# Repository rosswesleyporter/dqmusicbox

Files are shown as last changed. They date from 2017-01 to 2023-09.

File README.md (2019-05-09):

# Dementia Friendly Music Player

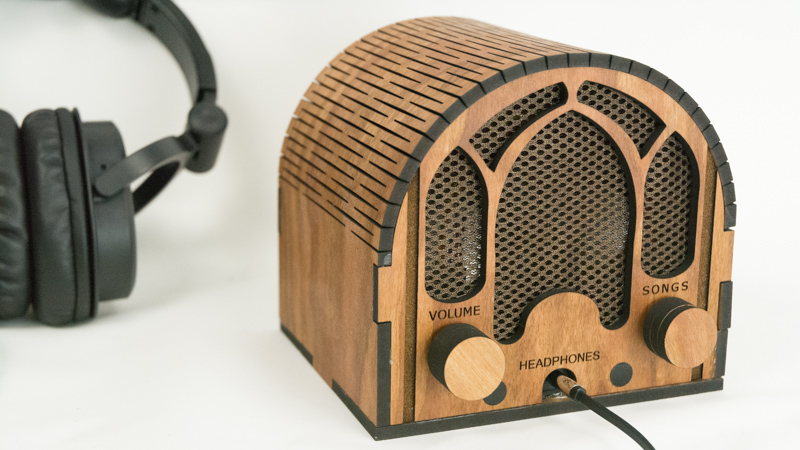
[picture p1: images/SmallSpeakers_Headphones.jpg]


I was inspired by the documentary Alive Inside, which shows the profound joy that music can bring to people with dementia. But my Dad could no longer operate CD players or iPods. But he could use this, because it operates like a familiar 1940s radio (but with a Pi & music files inside). 

Goals: 
1. Bring the joy of music to those dementia 
2. Bring the joy of meaningful giving to makers 

47 million people worldwide have dementia. People with dementia often travel back in time by literally forgetting the most recent decades (and modern tech). Thus the vintage user interface of this device. 

The build process is easy -- no soldering, no woodworking. You can make this. Kids can make this.

You can choose between a wood enclosure (photo above) or a 3D printed enclosure. Special thanks to Trey Bagley for designing the gorgeous retro-style 3D printed enclosure.

Everything you need is in this repository e.g. software, build instructions, laser cutting (wood) files, and 3D printing files, detailed step-by-step build instructions with photos. If you have a laser cutter or a 3D printer, you can do this at home. Alternatively, you can send the files to an online service of your choice to laser cut or 3D print the enclosure.

For more information, see http://DementiaMusicPlayer.org.

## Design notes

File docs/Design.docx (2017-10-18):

# DQMusicBox: Design

17 October 2017

# 1 About this document

This document specifies the design for a dementia-friendly music player called DQMusicBox. It is an open source project. This document exists so other people can modify or improve on DQMusicBox. If you want to make a DQMusicBox from the existing design, you don’t need this document – you can follow the existing build instructions (readme.pdf).

# 2 Discussion

Let’s start where we left off in the requirements document – with some of the challenging use-cases. I have added a few key sentences about the design.

Use case | Challenge

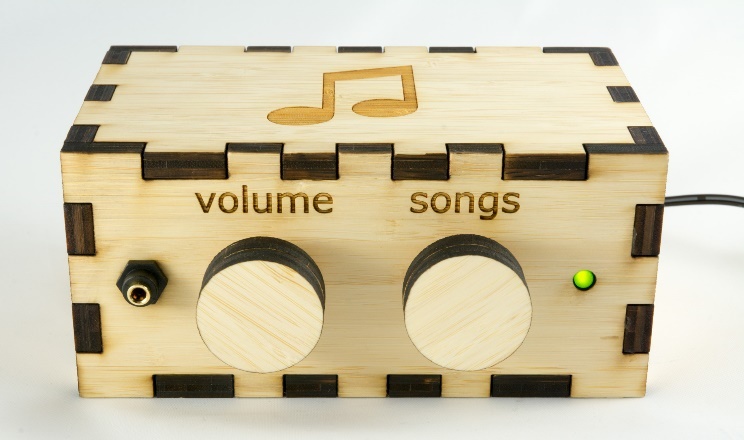
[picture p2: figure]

[End-user] Be familiar | The device should immediately seem familiar to the user. For instance, by resembling a vintage radio or a vintage phonograph (you may have better ideas than these). Design: Vintage radio.

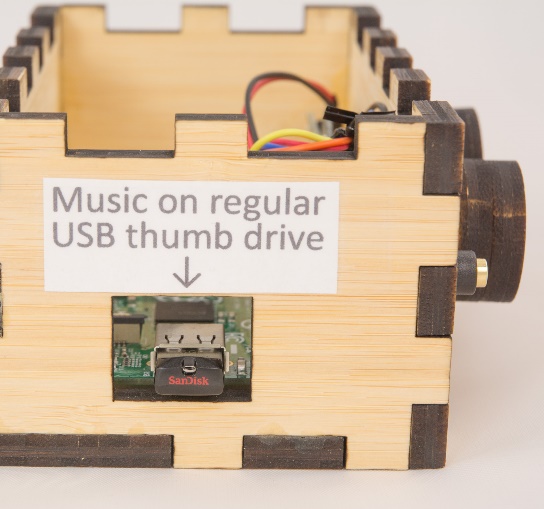
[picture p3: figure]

[Caregiver] Update the set of music | The caregiver may be a non-technical elderly spouse. Thus, mucking with micro-SD cards may not be the best choice. Design: An externally accessible normal USB thumb drive holds the music and only the music (the operating system and programs are stored elsewhere).
[System] Play key music formats | It’s helpful for the caregiver if the system supports a variety of music formats e.g. MP3, AAC/iTunes, FLAC. Design: VLC (https://www.videolan.org/vlc/index.html) (specifically VLC-NOX) handles the playback, so all of the above formats are supported.
[System] Create playlist | Create a playlist in some sensible order e.g. alphabetical by album/folder name. Design: My code scans the USB thumb drive, orders found music by album/folder name, and then hands this off as a single playlist to VLC-NOX.
[System] Have good audio quality | The sound quality should at least be good. It doesn’t have to be amazing, but it shouldn’t be aggravating. Design: The system uses a firmware update (https://www.raspberrypi.org/forums/viewtopic.php?f=29&t=136445) from the Raspberry Pi Foundation that dramatically improves audio quality, details below.
[System] support sudden shutdown | The device should behave like a consumer electronics device e.g. you can unplug it with no issues. Design: The system uses a read-only micro-SD card. More specifically, a TMP_WRITE_PROTECT (https://www.seanet.com/~karllunt/sdlocker.html) micro-SD card.

# 3 Key hardware components

## 3.1 List of hardware components

For a full list of hardware components, see the build instructions (readme.pdf). Below are a few of the key hardware components.

## 3.2 How did you choose key components?

When my wife asks me a question, sometimes I say, “It’s a long nerdy answer, do you really want to know?”. Then she usually leaves the room. Do you want to know the long answer? If so, read on. The choice was largely driven by satisfying the above challenging use-cases. And by cost. And I used the decision grid table below. The decision grid is 1.5 years out of date, but gives you a sense.

| Parts cost including case | Ease of loading music | Unpluggable? | Quick boot? | Software effort | Hardware design effort | Soldering | Support | audio quality | Total | Notes
Score range | 3 = $50 or less 2 = $65 or less 1 = $80 or less 0 = $95 or less | 2 = USB flash 1 = ext SD 0 = int SD | 2 = safe 1 = mostly safe 0 = crashola | 1 = instant 0 = <1 min | 2 = no coding 1 = some coding 0 = all coding | 2 = none 1 = some 0 = all | 2 = little 1 = some 0 = lots | 2 = great 1 = OK 0 = none
Score weight | 2 | 1 | 1 | 1 | 1 | 2 | 1 | 1
Pi 2 (https://www.raspberrypi.org/products/raspberry-pi-2-model-b/) | 1 | 2 | 1 | 0 | 2 | 2 | 2 | 2 | G | 15
Pi A+ (https://www.raspberrypi.org/products/model-a-plus/) | 2 | 1 | 1 | 0 | 2 | 2 | 2 | 2 | G | 16
Pi Zero (https://www.raspberrypi.org/products/pi-zero/) | 3 | 1 | 1 | 0 | 2 | 2 | 0 | 2 | G | 16
Banana Pi (http://www.s-config.com/goodbye-raspberry-pi-hello-banana-pi/) | 1 | 2 | 1 | 0 | 1 | 2 | 2 | 1 | G | 13
Arduino + Adafruit MP3 shield (https://www.adafruit.com/products/1790) | 1 | 1 | 2 | 1 | 0 | 2 | 0 | 2 | G | 12 | MP3 shield is $30.
Arduino + Sparkfun MP3 shield (https://www.sparkfun.com/products/12660) | 1 | 1 | 2 | 1 | 0 | 2 | 0 | 2 | G | 12 | MP3 shield is $35.
Arduino + Elechouse MP3 shield (http://www.gearbest.com/boards-shields/pp_241522.html?currency=USD) | 2 | 2 | 2 | 1 | 0 | 2 | 2 | 1 | G | 16 | MP3 shield is $20. Poor playlisting.
Sparkfun Lilypad (https://www.sparkfun.com/products/11013) | 0 | 0 | 2 | 1 | 0 | 2 | 1 | 2 | G | 10 | Lilypad is $50.
Custom standalone circuit (http://pcbshopper.com/) | 3 | 2 | 2 | 1 | 2 | 0 | 1 | 1 | G | 15
MP3 hardware player | | | | | | | | | | | Can't find good one
Pine64 (http://pine64.com/) | 3 | 2 | 1 | 0 | 1 | 2 | 2 | 1 | ? | 16 | Has headphone jack.
C.H.I.P. (http://getchip.com) | 3 | 2 | 1 | 0 | 1 | 2 | 2 | 1 | ? | 16 | $9. Has headphone jack.
Orange Pi PC (http://hackaday.com/2015/09/05/orange-is-the-new-15-pi/) | 2 | 2 | 1 | 0 | 1 | 2 | 2 | 0 | N | 14 | OK built-in audio
Odroid C1+ (http://www.hardkernel.com/main/products/prdt_info.php?g_code=G143703355573) | | | | | | | | | | | No headphone jack.

## 3.3 Raspberry Pi 1 Model A+

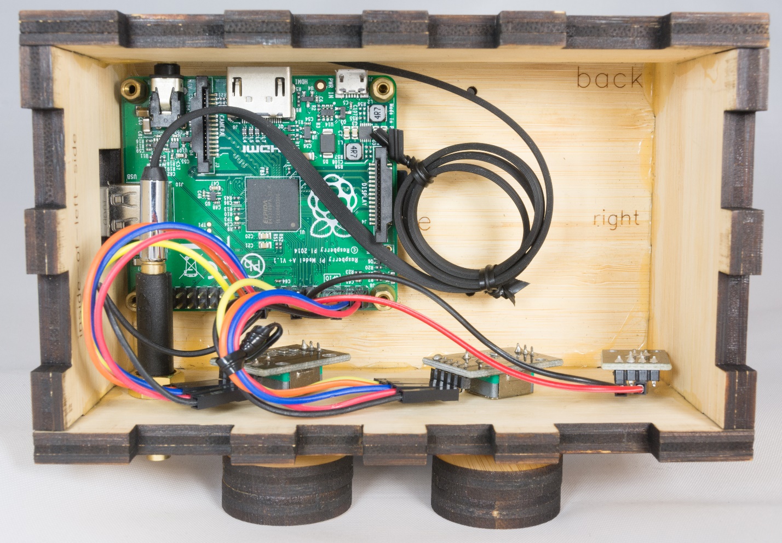
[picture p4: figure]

- Why Pi? A Pi satisfied the challenging use-cases above.
- Why Pi A+? Cheapest Pi model that has a headphone jack and populated USB headers.

## 3.4 KY-040 rotary encoder

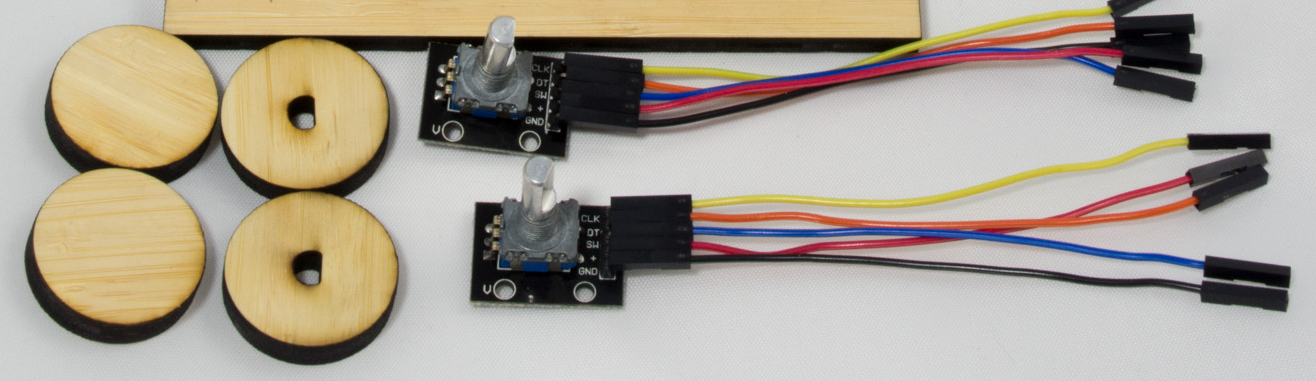
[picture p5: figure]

- Why?
  - No soldering required! Just jumper wires.
  - Performs well.

## 3.5 Making the micro-SD card reliable -- TMP_WRITE_PROTECT

The micro-SD card is the weak link in Raspberry Pi based solutions. For instance, micro-CD cards can get corrupted when power is lost during a write. But what if we didn’t need to write? That is the case here – the DQMusicBox doesn’t need to change. DQMusicBox is a fixed function device – it doesn’t have to evolve. So the micro-SD card can be read-only. Raspbian doesn’t really want to be read-only. But I don’t care if Raspbian is unhappy. I only care if it works.

The answer is the TMP_WRITE_PROTECT feature that is part of the SD card spec. It is fiendish. It accepts write requests (like Raspbian wants), but it puts all such writes in a special place. And those writes are thrown away when power is lost or when the device is rebooted. So no worries, if power is lost during a write. And if you want to factory reset a DQMusicBox? Just unplug it. References:

  - SD Card Write Protection (http://www.bertold.org/sdtool/)
  - Build the SD Locker and Make Your SD Cards More Secure

I know of two methods to enable TMP_WRITE_PROTECTION:

1. Building the SD locker project on Hackaday (https://d.docs.live.net/607157b747fa4bbf/Documents/projects/dqmusicbox_working/docsource/Build%20the%20SD%20Locker%20and%20Make%20Your%20SD%20Cards%20More%20S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).
2. Follow Appendix 1 in this project’s build instructions. The essence of it is to use a Pi 3, booted from USB, using the SD Card Write Protection (http://www.bertold.org/sdtool/) too. This is the method that I used.

# 4 Software stack (component diagram)

I like to think of myself as intelligently lazy. And I think that I achieved that here. The project makes good use of existing code. In particular, VLC does a lot of the work. I wrote a shell script and ~300 lines of Python. Thanks to Bob Rathbone (http://bobrathbone.com/) for his excellent tutorial on rotary encoders and for his GPL’ed code (http://www.bobrathbone.com/raspberrypi/Raspberry%20Rotary%20Encoders.pdf).

# 5 Use-case implementation

I’ve already covered the challenging use-cases. Here are the others.

## 5.1 End-user

Name | Description
Start song | Turn a knob, any knob
Change song | Turn the songs knob – clockwise for next, anti-clockwise for previous
Change volume | Turn the volume knob

## 5.2 Caregiver

Name | Description
Pause music | Tap either knob.
Update the set of music | Use a PC or Mac to add or remove albums/folders from the USB thumb drive.

## 5.3 Builder

Name | Description
Support builders that are not woodworkers | We don’t need no stinking jigsaws, we have lasers! The case is laser cut, pieces just need to be glued together. You can send the design to a company that does the laser cutting for you for $28.
Support builders that are not good at soldering | No soldering required. The key was finding rotary encoders that don’t require soldering.

## 5.4 System

Name | Description
Be secure | This is not an Internet of Things device. This is a thing. It never has to be online, it never has to be exposed to nasty things like hackers and reality television.

# 6 Wiring diagram

# 7 Case design

The requirements and key elements of the design for the case:

- Keep with the theme of vintage radio
- Use a laser-cutter approach, so no woodworking skills are required
- Make it possible to send off the design to a company (e.g. Ponoko) for laser cutting (not everyone has access to a laser cutter)
- No staining, painting, or other finishing required
- Include engraving (“volume”, “songs”, and the musical note)
- Include knobs
- Wood thicker than the screw threads of the standoffs (the screws that hold the Pi in place)
- Not too expensive

The result is a design intended to be laser-cut from two pieces of 181x181mm 6.7mm thick amber bamboo (https://www.ponoko.com/make-and-sell/show-material/567-bamboo-blonde-3-ply):

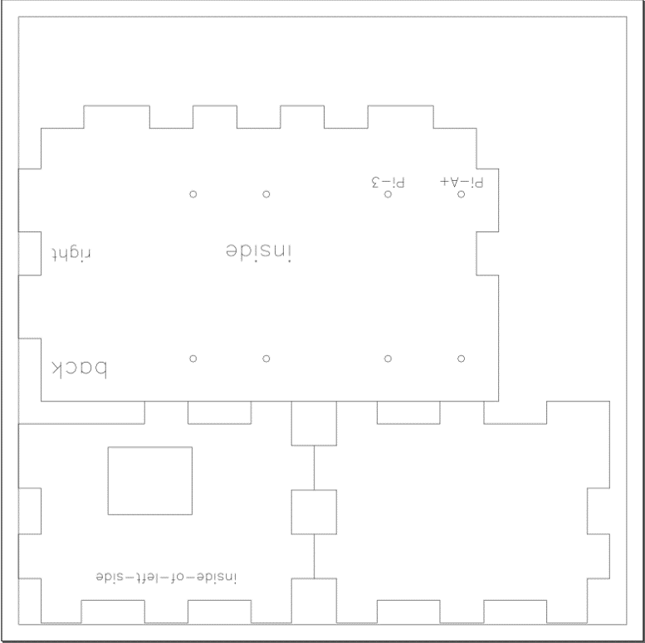
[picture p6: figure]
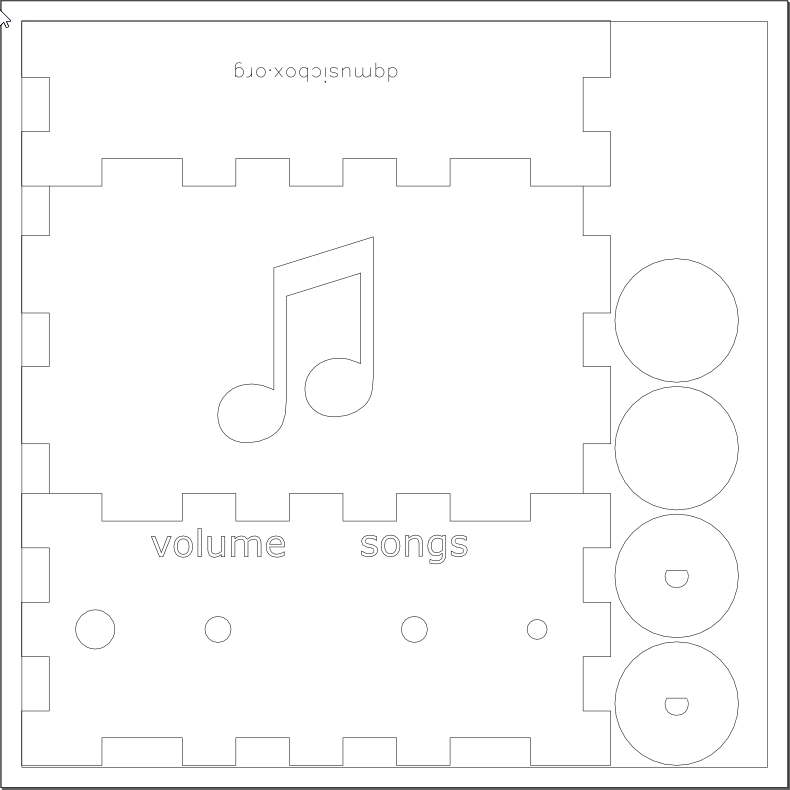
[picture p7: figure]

The actual case design can be found in github (https://github.com/rosswesleyporter/dqmusicbox/tree/master/case).

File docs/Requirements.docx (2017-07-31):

# DQMusicBox: Requirements

30 July 2017

# 1 About this document

This document specifies the requirements for a dementia-friendly music player called DQMusicBox. It is an open source project. This document exists so other people can modify or improve on DQMusicBox. If you want to make a DQMusicBox from the existing design, you don’t need this document – you can follow the existing build instructions (readme.pdf).

# 2 Why I created this project

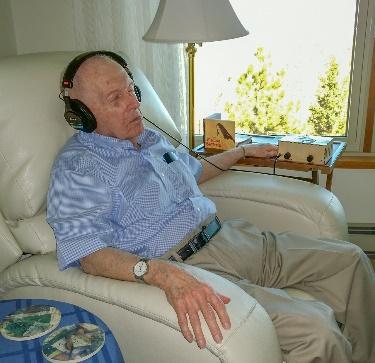
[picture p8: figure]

That’s DQ in the photo – my Dad. I was inspired by the documentary Alive Inside (http://www.aliveinside.us/) -- it suggests that people with dementia come alive when listening to their favorite music. Following that suggestion, I put DQ’s favorite music on an iPad. There was sustained joy on his face – joy from the familiar music and joy from the fact that nothing else in the frustrating world mattered for a few minutes. Unfortunately, he could no longer operate a traditional stereo or an iPad. Happily, he could use the music box that I later made for him.

# 3 The end-user’s special requirements

## 3.1 The device must feel familiar – no new learning

A key hypothesis is that the end-user interface must be simple and familiar. In other words, it needs to be easy *and* not require new learning. Every person with dementia is different, but it is common for the old memories to be stronger than the new memories. Thus, the device would ideally be familiar in the sense of being like a device from the end-user’s youth e.g. a vintage radio or a vintage phonograph. You may not agree with this hypothesis, and that’s OK -- you may also have different ideas or requirements. But this hypothesis is part of my requirements, so I’m making it clear.

## 3.2 The end-user needs a playlist of favorites, not a vast library

The end-user doesn’t need to have a lot of music on the device at any given time. Perhaps 50 old favorite songs. In modern terms, the end-user needs a playlist. Happily, this means that music selection is easier to implement – fewer songs to scroll through or otherwise navigate through. That said, the caregiver will want to change the set of music from time to time. By contrast, you probably use a cloud music service and have access to essentially an unlimited number of songs. That is a much harder navigation problem.

# 4 Use-cases

## 4.1 End-user

To keep things easy for the end-user with dementia, there are only three end user use-cases.

Name | Description
Be familiar | The device should immediately seem familiar to the user. For instance, by resembling a vintage radio or a vintage phonograph (you may have better ideas than these).
Start song | Start music playing
Change song | For instance, go to next song or prior song
Change volume | Make louder or softer

## 4.2 Caregiver

The caregiver is whoever setups up the device or helps the end-user with the device.

Name | Description
Pause music | Ideally should be possible both explicitly (e.g. a button press) and automatically (e.g. an automatic time-out).
Update the set of music | Add/remove music, including when preparing the device for first use. The caregiver will want to change the set of music from time to time, but not necessarily often.

## 4.3 Builder

This is a DIY project, so there is a builder. You may disagree, but I want as many people as possible to be able to build this. Thus:

Name | Description
Support builders that are not woodworkers | The DIY build plans should not require woodworking skills or woodworking tools.
Support builders that are not good at soldering | The DIY build plans should not require soldering skills or soldering tools.

## 4.4 System

Name | Description
Have good audio quality | Sound quality should be at least good.
Create playlist | The songs should play in some sensible order e.g. alphabetical by album name. In other words, the system needs to scan for music files and put them in some sensible order.
Play key music formats | e.g. MP3, AAC/iTunes, FLAC
Support sudden shut down | The device should tolerate being unceremoniously unplugged. That is, it should behave like any other consumer audio device.
Be secure | The device should have a known security plan. That plan could be that the device is not connected to a network. If the device runs a full operating system (Linux, Windows, …) and is connected to a network then it should get regular security patching, ideally without caregiver intervention.

# 5 Discussion

The need is simple, so the requirements are short. But there are challenges implied by these requirements.

Use case | Challenge
[Caregiver] Update the set of music | The caregiver may be a non-technical elderly spouse. Thus, mucking with micro-SD cards may not be the best choice. A USB thumb drive could be OK.
[System] Play key music formats | It’s helpful for the caregiver if the system supports a variety of music formats e.g. MP3, AAC/iTunes, FLAC. Not a problem if the device uses a full operating system e.g. Raspbian. But it is challenging for MP3 player boards and Arduino.
[System] Create playlist | Create a playlist in some sensible order e.g. alphabetical by album/folder name. Sounds easy, ya? And it is in the context of a full operating system e.g. Raspbian. It is surprisingly not straightforward for MP3 player boards and Arduino.
[System] Have good audio quality | The sound quality should at least be good. It doesn’t have to be amazing, but it shouldn’t be aggravating. This is not a problem for most technology options, but it is a challenge for some.
[System] support sudden shutdown | The device should behave like a consumer electronics device e.g. you can unplug it with no issues. This is no problem for MP3 player boards and Arduino. If the device includes a battery, it’s also no problem for a full operating system e.g. Raspbian. If the device does not have a battery, then sudden shutdown is a challenge for a full operating system. Because this is a fixed-function device, one option is for the executable bits to be on a read-only device (to resist corruption), keeping the music on a separate writeable device.

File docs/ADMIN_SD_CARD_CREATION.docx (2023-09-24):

# Dementia Friendly Music Player: How to prepare the micro-SD card image

24 September 2023

# 1 Introduction

This document describes how to create a Dementia Friendly Music Player system image – a .img file. I (Ross) am probably the only person that needs this document. Mostly people making a Dementia Friendly Music Player will use the fruit (the .img file) of the process described here -- you don’t need to create your own custom .img file unless you really want to.

# 2 No warranty

USE THESE DEMENTIA FRIENDLY MUSIC PLAYER (DQMUSICBOX) PLANS AND SYSTEM AT YOUR OWN RISK. THE DEMENTIA FRIENDLY MUSIC PLAYER PLANS ARE PROVIDED AS IS WITHOUT WARRANTY OF ANY KIND EITHER EXPRESSED OR IMPLIED, INCLUDING, BUT NOT LIMITED TO, THE IMPLIED WARRANTIES OF MERCHANTABILITY AND FITNESS FOR A PARTICULAR PURPOSE. THE ENTIRE RISK AS TO THE QUALITY AND PERFORMANCE OF THE PLANS AND SYSTEM IS WITH YOU. SHOULD THE PLANS OR SYSTEM PROVE DEFECTIVE, YOU ASSUME THE COST OF ALL NECESSARY SERVICING, REPAIR OR CORRECTION. IN NO EVENT WILL ANY PARTY BE LIABLE TO YOU FOR DAMAGES, INCLUDING ANY GENERAL, SPECIAL, INCIDENTAL OR CONSEQUENTIAL DAMAGES ARISING OUT OF THE USE OR INABILITY TO USE THE PLANS OR SYSTEM.

# 3 To create built-in headphone jack version

The Dementia Friendly Music Players below use the Pi’s built-in headphone jack.

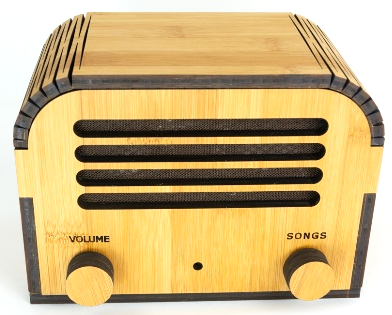
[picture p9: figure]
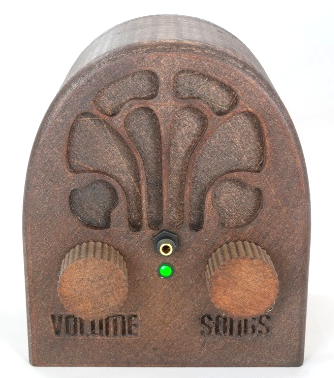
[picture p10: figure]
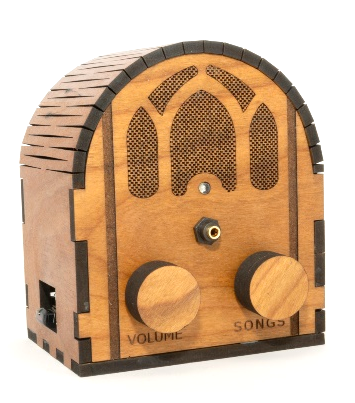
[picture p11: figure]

## 3.1 Flash DietPi onto the micro-SD card

Install DietPi i.e. follow these instructions: https://dietpi.com/docs/install/. I used DietPi 8.21.0 which was current as of this writing in September 2023. I used balenaEtcher (https://etcher.io/) (free) to write the disk image to the micro-SD card. This may take a while as the system updates itself.

## 3.2 Boot & configure DietPi

Put the Pi on Ethernet. Move the micro-SD card to the Pi, boot DietPi. After a build process (which will take a while), you will be prompted to make some choices.

DietPi-Config

Audio Options: Enable : Install ALSA to enable audio capabilities

Audio Options: Sound Card : Onboard 3.5mm output

DietPi-Software

Hardware Projects : Python 3 RPi.GPIO

System: ALSA : Advanced Linux Sound Architecture

Development : Git : clone and manage …

Development : Python 3: Runtime system, pip package installer, …

Install

## 3.3 Install pmount

sudo apt-get install pmount

## 3.4 Install VLC (music player)

sudo apt-get install vlc-bin

sudo apt-get install vlc-plugin-base

## 3.5 adduser pi

sudo adduser pi

## 3.6 Install/clone dqmusicbox, enable

cd /home/pi

git clone --depth 1 https://github.com/rosswesleyporter/dqmusicbox/

sudo chmod 755 dqmusicbox/bin/dqmusicbox.py

## 3.7 Install Python bindings for VLC

cd /home/pi

sudo git clone https://github.com/oaubert/python-vlc

cp python-vlc/generated/2.2/vlc.py dqmusicbox/bin

chmod 755 dqmusicbox/bin/vlc.py

## 3.8 Add shell script to automatically start dqmusicbox

cd /home/pi

sudo cp dqmusicbox/bin/dqmusicbox.sh /etc/init.d

sudo chmod 755 /etc/init.d/dqmusicbox.sh

sudo update-rc.d dqmusicbox.sh defaults

For more information, see Stephen Christopher Phillips’ terrific page (http://blog.scphillips.com/posts/2013/07/getting-a-python-script-to-run-in-the-background-as-a-service-on-boot/).

## 3.9 Configure such that USB drives mount automatically

The instructions below are from pauliucxz (https://raspberrypi.stackexchange.com/users/66022/pauliucxz) in StackExchange 66169 (https://raspberrypi.stackexchange.com/questions/66169/auto-mount-usb-stick-on-plug-in-without-uuid), preserved below for clarity. I am quite thankful for that answer. The first USB drive will automatically mount as /media/usb1.

Specify a udev rule by creating file /etc/udev/rules.d/usbstick.rules

ACTION=="add", KERNEL=="sd[a-z][0-9]", TAG+="systemd", ENV{SYSTEMD_WANTS}="usbstick-handler@%k"

Configure a system service by creating file /lib/systemd/system/usbstick-handler@.service

[Unit]

Description=Mount USB sticks

BindsTo=dev-%i.device

After=dev-%i.device

[Service]

Type=oneshot

RemainAfterExit=yes

ExecStart=/usr/local/bin/cpmount /dev/%I

ExecStop=/usr/bin/pumount /dev/%I

Create the mount script file /usr/local/bin/cpmount

#!/bin/bash

if mountpoint -q /media/usb1

then

if mountpoint -q /media/usb2

then

if mountpoint -q /media/usb3

then

if mountpoint -1 /media/usb4

then

echo "No mountpoints available!"

#You can add more if you need

else

/usr/bin/pmount --umask 000 --noatime -w --sync $1 usb4

fi

else

/usr/bin/pmount --umask 000 --noatime -w --sync $1 usb3

fi

else

/usr/bin/pmount --umask 000 --noatime -w --sync $1 usb2

fi

else

/usr/bin/pmount --umask 000 --noatime -w --sync $1 usb1

fi

Make the script executable

sudo chmod 755 /usr/local/bin/cpmount

## 3.10 Reboot

sudo reboot

## 3.11 Test

Make sure the music plays…

## 3.12 Shutdown

Provided that the reboot went well, shutdown:

sudo shutdown –h now

Then remove the micro-SD card.

## 3.13 Use Win32DiskImager to create the master image

Remove the micro-SD card from your Pi and place in the card reader of your computer. Use Win32DiskImager to create an image of Dementia Friendly Music Player that you just nicely configured.

# 4 To create USB DAC version

The Dementia Friendly Music Player that looks like this uses a USB DAC.

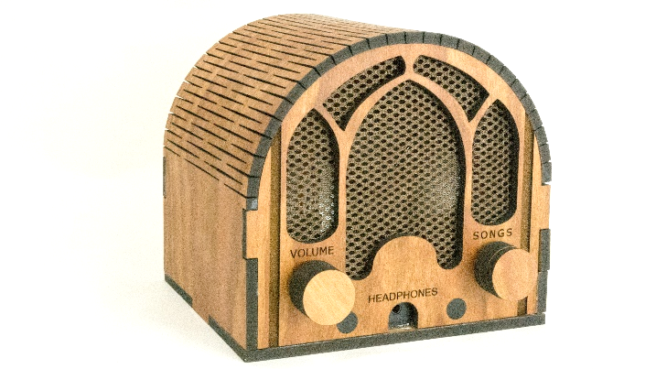
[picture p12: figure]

Use the image that you created above for the headphone version and make this change:

dietpi-config

Audio Options: Sound Card : USB Audio DAC (any)

Remove the micro-SD card from your Pi and place in the card reader of your computer. Use Win32DiskImager to create an image of Dementia Friendly Music Player that you just nicely configured.

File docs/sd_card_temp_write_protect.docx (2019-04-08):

# How to Write Protect an SD Card

7 April 2019, http://DementiaMusicPlayer.org, Ross Porter rosswesleyporter@gmail.com

## About SD card write protection TMP_WRITE_PROTECT

This step is optional. It will increase the durability of the system. If you or your friend already work with Raspberry Pis, you may find this fun. If you don’t then you might find this frustrating and it’s perfectly OK to skip this optional step.

About TMP_WRITE_PROTECT:

- Raspbian and DietPi, don’t generally like to be rudely shut down i.e. having the power plug pulled.
- Rude power downs can interrupt writes to the micro SD card and potentially corrupt the OS.
- But we have a special case here, because DQMusicBox does not need to be online and does not need to be updated. In other words, it is safe to write protect the micro SD card.
- The SD card standard has a rarely used feature known as TMP_WRITE_PROTECT (which is a useful google search term) i.e. temporary write protection.
- When in this mode, the SD accepts write accepts write requests, but any such writes are made to temporary storage and are deliberately lost upon reboot or power loss.
- In other words, if you pull the plug on a DQMusixBox you are effectively doing a factory reset. Music stored on the USB thumb drive is unaffected.
- To enable this, set the TMP_WRITE_PROTECT bit in the Card Specific Data on micro-SD card (more on this below).
- Here is the SD Association’s official description of TMP_WRITE_PROTECT from the SD Specifications Part 1 Physical Layer Simplified Specification Version 6.00 (https://www.sdcard.org/downloads/pls/pdf/index.php?e=EN_SS1): Temporarily protects the entire card content from being overwritten or erased (all write and erase commands for this card are temporarily disabled). This bit can be set and reset. The default value is 0, i.e. not write protected.
- For the curious, here are some of the other fields in the Card Specific Data, chart taken from the same document linked just above:

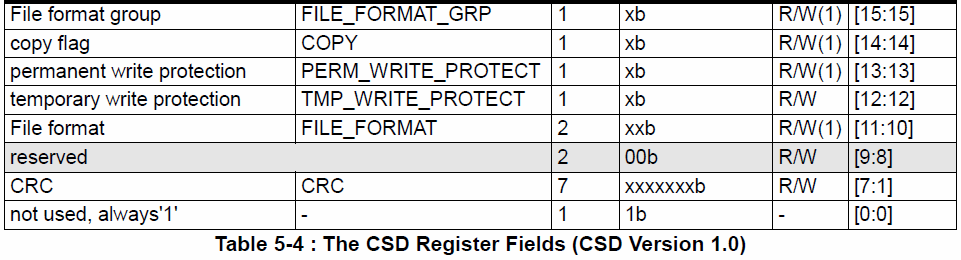
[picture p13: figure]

- References:
  - SD Card Write Protection (http://www.bertold.org/sdtool/)
  - Build the SD Locker and Make Your SD Cards More Secure

## Option 1: Build the SD locker project

There are several ways to implement TMP_WRITE_PROTECT. I was originally inspired by the SD locker project on Hackaday (http://hackaday.com/2013/11/12/keep-your-sd-cards-data-safe-with-the-sd-locker/) and by its successor (https://www.seanet.com/~karllunt/sdlocker2.html). Both of which look like fun. But I ended up using Option 2 below as it is more consistent with Raspberry Pi work.

## Option 2: Use a Raspberry Pi 3

This is the option that I used. In brief, the write protection process is:

1. Write the DQMusicBox image to a micro-SD card, as per the instructions above.
2. Boot a Raspberry Pi 3 from a USB thumb drive.
3. Once booted, insert a micro-SD card and issue the following command: sudo ./sdtool/static/arm-sdtool /dev/mmcblk0 lock

This is my setup for doing so:

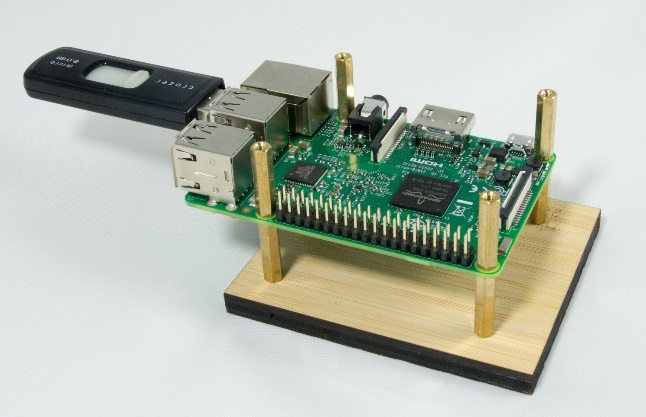
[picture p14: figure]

The slightly tricky bit is to get the Raspberry Pi 3 to boot from USB. See below for the process that I used to create to create the setup above. You will only have to do this once.

1. You’ll need:
  a. A Raspberry Pi 3. I keep a Pi 3 just for this purpose i.e. I don’t use this Pi 3 inside a DQMusicBox.
  b. A good USB thumb drive. I keep a thumb drive just for this purpose. Apparently this won’t work with some low performance USB thumb drives, although it worked with my old 2GB thumb drive (pictured above). I now use a SanDisk Extreme 32GB thumb drive (https://www.amazon.com/gp/product/B00KT7DXIU/ref=oh_aui_detailpage_o00_s00?ie=UTF8&psc=1).
  c. A micro-SD card. You will only need for 30 minutes to complete the steps below, then you can use the card for other purposes.
2. Download DietPi (http://dietpi.com/).
3. Write the DietPi image to the micro-SD card (using Etcher or Win32diskimager).
4. Write the same DietPi image to the USB thumb drive.
5. Attach Ethernet to your Raspberry Pi 3.
6. Insert the micro-SD card.
7. Start the DietPi installation process i.e.:
  a. Boot the Pi 3 from the micro-SD card
  b. Connect to the Pi 3 over the network with Putty or something similar, login with username=root password=dietpi
8. After a while, you will get to this screen, choose DietPi-Config

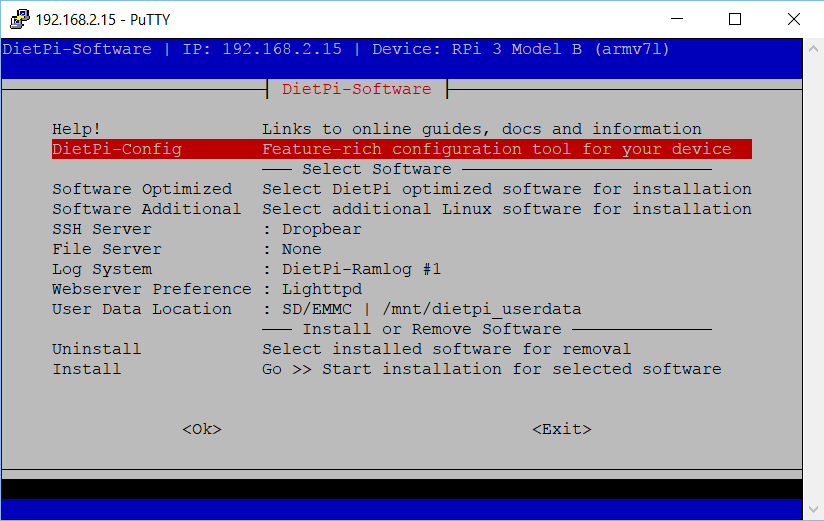
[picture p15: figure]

9. Choose Advanced Options:

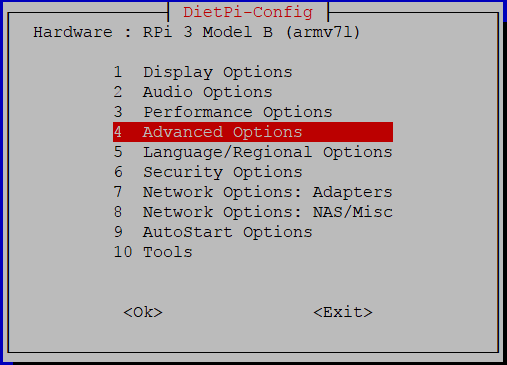
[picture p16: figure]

10. Choose USB boot support and choose to enable it:

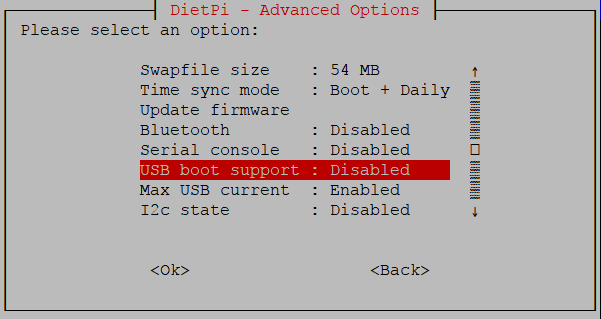
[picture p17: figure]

11. Choose OK (read the full message first):

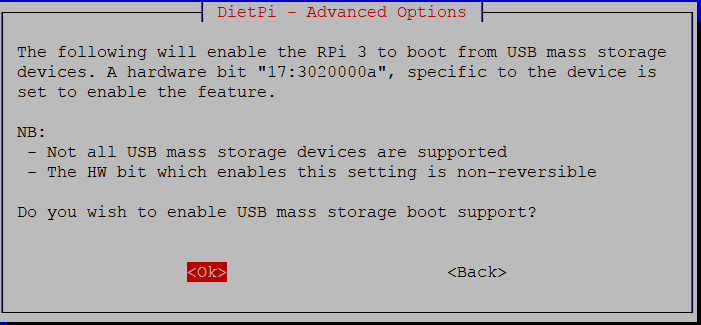
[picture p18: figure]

12. Choose Yes to reboot:

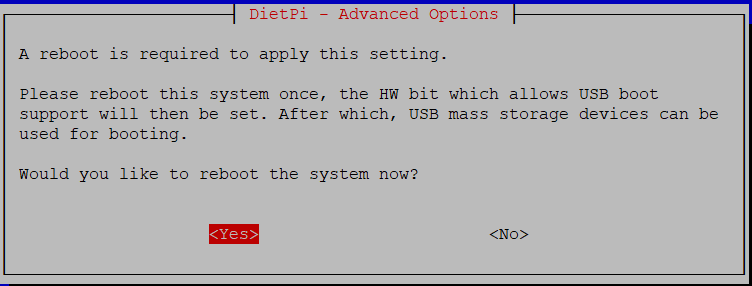
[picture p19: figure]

13. After rebooting, choose Install:

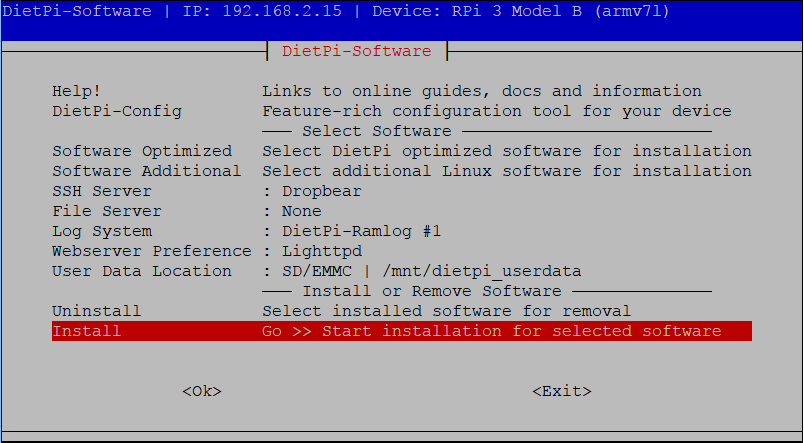
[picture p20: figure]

14. Let the installation run and finish.

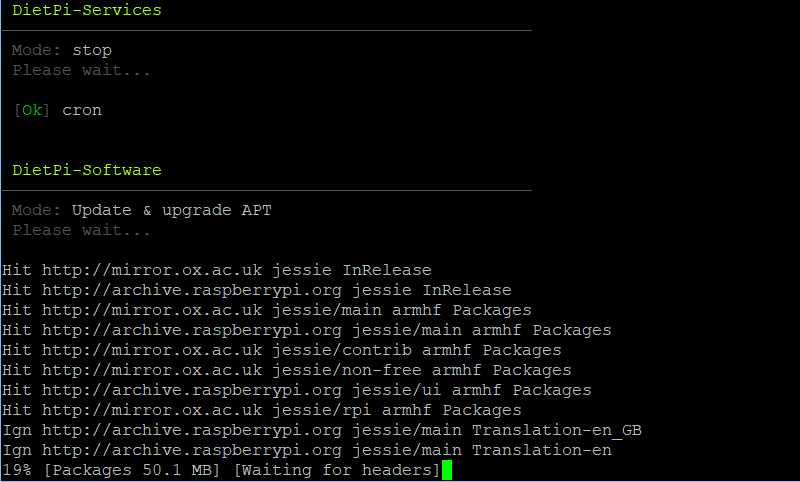
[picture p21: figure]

15. Once the installation is complete, switch to a USB setup:
  a. Unplug the Pi.
  b. Remove the micro-SD Card.
  c. Insert the USB thumb drive.
  d. Plug the Pi back in and boot.
16. Install DietPi on the USB thumb drive. Start by letting DietPi update itself:

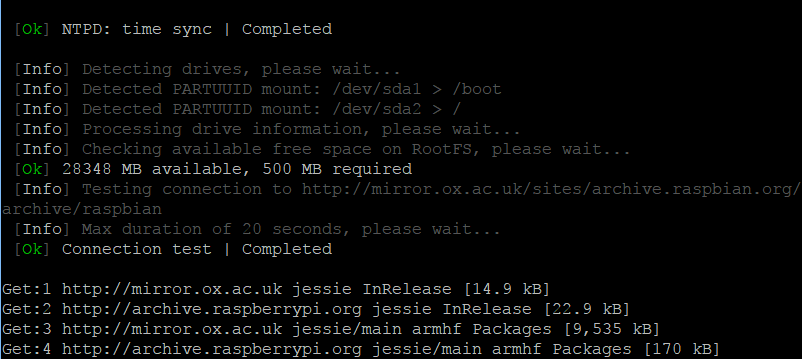
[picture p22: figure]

17. When prompted, restart your Pi:

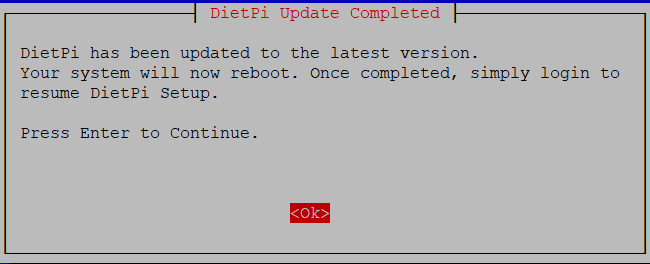
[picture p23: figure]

18. Install:

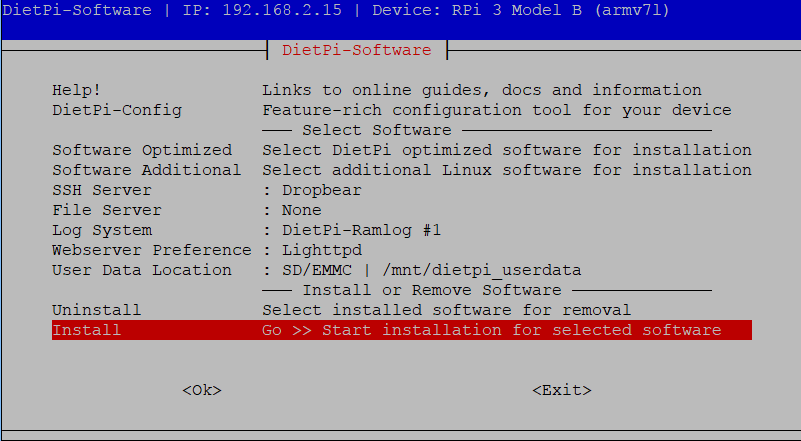
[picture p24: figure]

19. Let DietPi do more updating:

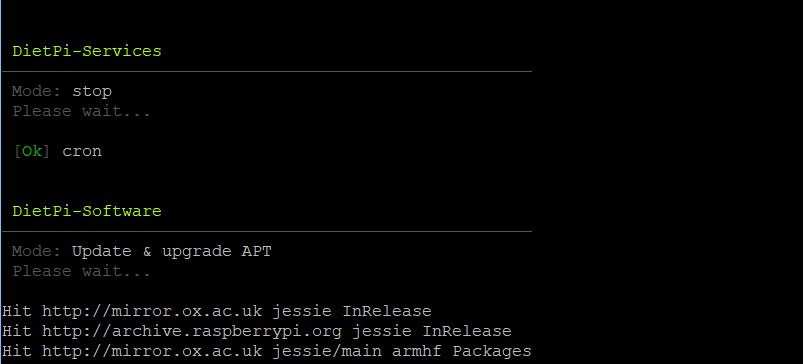
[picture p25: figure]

20. DietPi will reboot to complete the installation, then you’ll get a normal command prompt:


21. Install git with sudo apt-get install git
22. Get the write protection tool sdtool (https://github.com/BertoldVdb/sdtool/blob/master/static/arm-sdtool) with git clone https://github.com/BertoldVdb/sdtool
23. Put an micro-SD card in the slot, practice enabling TMP_WRITE_PROTECT: sudo ./sdtool/static/arm-sdtool /dev/mmcblk0 lock
24. Now practice reversing the above: sudo ./sdtool/static/arm-sdtool /dev/mmcblk0 unlock
25. You are done!

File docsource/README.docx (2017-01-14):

# DQMusicBox - music player for people with dementia

# How to build one – it’s easy

14 January 2017, rosswesleyporter@gmail.com


My Dad could not operate normal music players. But he could operate this music player because it operates like a familiar two-knob radio. My son & I were inspired to design this by the documentary Alive Inside (http://www.aliveinside.us/) which shows the profound joy felt by some people with dementia when listening to their favorite music.

It’s easier than you think to make one. Everything I did (e.g. software, wood case design) is open source. This document contains all the information you need. You can order the parts online. No soldering required.


Parts cost | $130 - $170 depending on options + tax + shipping most parts from Amazon, includes headphones.
Music cost | Minimal as you should use the recipient’s existing music collection.
Build time | About three hours, once you have the parts & music.
Parts source | All parts can be mail ordered, links below.
Soldering? | No.
Command-line Linux? | No.
Tools needed | A computer with an SD card reader, fingers.
Laser cutter needed? | No. You can mail order the pre-cut pieces for the wood case.
Beverage? | Yes. I recommend a hoppy IPA while you are assembling.

# 1 Preview of the steps

Complete Beethoven Edition, Vol. 1: Symphonies

1) Order parts from Amazon, eBay, Ponoko | 2) Assemble recipient’s favorite music | 3) Copy software to micro-SD card


4) Receive parts from Ponoko | 5) Glue case together | 6) Screw in front panel items


7) Place Pi | 8) Connect wires | 9) Enjoy

# 2 No warranty

USE THESE DQMUSICBOX PLANS AND SYSTEM AT YOUR OWN RISK. THE DQMUSICBOX PLANS ARE PROVIDED AS IS WITHOUT WARRANTY OF ANY KIND EITHER EXPRESSED OR IMPLIED, INCLUDING, BUT NOT LIMITED TO, THE IMPLIED WARRANTIES OF MERCHANTABILITY AND FITNESS FOR A PARTICULAR PURPOSE. THE ENTIRE RISK AS TO THE QUALITY AND PERFORMANCE OF THE PLANS AND SYSTEM IS WITH YOU. SHOULD THE PLANS OR SYSTEM PROVE DEFECTIVE, YOU ASSUME THE COST OF ALL NECESSARY SERVICING, REPAIR OR CORRECTION. IN NO EVENT WILL ANY PARTY BE LIABLE TO YOU FOR DAMAGES, INCLUDING ANY GENERAL, SPECIAL, INCIDENTAL OR CONSEQUENTIAL DAMAGES ARISING OUT OF THE USE OR INABILITY TO USE THE PLANS OR SYSTEM.

# 3 Acknowledgements

People were very generous with their time, and I really enjoyed the experience. This is certainly an incomplete list: Alex & Mike & others at Ada’s (http://blog.seattletechnicalbooks.com/), the super smart staff at Metrix (http://www.metrixcreatespace.com/), neighbor Randy, Stephen Christopher Phillips (http://scphillips.com/), Bob Rathbone (http://www.bobrathbone.com/), Stephen Rusk (http://www.stephenrusk.com/), Graham Hill (http://www.ted.com/speakers/graham_hill), support at Ponoko (https://www.ponoko.com/), and my son.

# 4 Change log

v1.0, November 2015 | Original release
v1.1, September 2016 | - Changed music storage from a micro-SD memory card to a conventional USB memory stick. - Changed the base Operating System from full Raspbian to DietPi (http://dietpi.com/) – much smaller, so faster to boot, and less to go wrong.
V1.2, January 2017 | - Changed from USB audio to Pi built-in audio, including a firmware update for excellent audio quality.

# 5 What DQMusicBox does

## 5.1 For the person with dementia

Name | Description & implementation
Start song | Turning either of the knobs will start music playing.
Change song | Turn the songs knob.
Change volume | Turn the volume knob.
Pause | Tap the volume knob. Note that this also happens automatically – music pauses if there are no knob events in one hour.

## 5.2 For you

Name | Description & implementation
Shut down | Pull the power plug or long hold (15-30 seconds) on the volume knob.
Reboot | Pull the power plug and re-insert or long hold (15-30 seconds) on the songs knob.
Add/remove music | By adding/removing files on the USB memory stick.

# 6 Things you don’t need to do

I have done a number of things for you. If you have done other projects, you might assume that you have to do the things below. But don’t. Unless you want to customize.

Don’t connect the Pi to a monitor and keyboard | There is no need to connect the Pi to a monitor and keyboard as part of this build process. In fact, the sound system can behave differently if a monitor is connected.
Don’t connect the Pi to a network | There is no need to connect the Pi to a network as part of this build process. Nor does the Pi need to be on a network to operate as a music player. In both cases this is deliberate – want to keep it simple and safe. That said, you can connect it to a network from time to time if you wish.
Don’t login to the Pi | You don’t need to. But if you wish to, the username=root password=dietpi i.e. unchanged from the DietPi defaults.
Don’t go to github | Everything is in the mini distribution that you will download below. But this is an open source project, so naturally everything is in github if you want to poke around. https://github.com/rosswesleyporter/dqmusicbox
Don’t put stain on the maple case | The maple case is the default wood case (see below). It’s a prefinished maple, so you don’t need to stain it. In fact, I don’t recommend adding stain because darkening the wood will reduce the legibility of the knob labels. If you order the birch case, different story. The birch case is unfinished. I suggest using a soft cloth to rub on some regular olive oil. That will provide a bit of protection and won’t reduce the legibility of the knob labels. I am not a woodworker. If you are a woodworker and have a better suggestion, I’d love to hear it.

# 7 Ordering the parts

## 7.1 Create a Ponoko account

Ponoko is a company that laser cuts wood and sends you the precisely cut pieces. You don’t need to use Ponoko – you are welcome to take my case design files to your local maker space and cut there. In other words, Ponoko is convenient but not necessary. To create a Ponoko account:

1. Go to https://www.ponoko.com/
2. Choose “Get Making”

## 7.2 Order the parts

Link to order item | Notes | Alternatives
DQMusicBox wood case (maple veneer) (http://www.ponoko.com/design-your-own/products/dqmusicbox-case-maple-12981) | From the linked page, choose “Add to Personal Factory”. | The birch veneer case (http://www.ponoko.com/design-your-own/products/dqmusicbox-birch-13918) is $25 less, but the wood is unfinished. Or do the laser cutting yourself.
Raspberry Pi 3 Complete Starter Kit (the brains) (https://www.amazon.com/gp/product/B01IYC0LT0/ref=oh_aui_detailpage_o00_s00?ie=UTF8&psc=1) | Includes a Raspberry Pi 3, plastic case, power supply, micro-SD card. And an unneeded heat sink. | You can also use a Pi 2 or a Pi A+. You will need a small case, power supply and micro-SD card.
KY-040 rotary encoder knobs (http://www.ebay.com/itm/172155425854?_trksid=p2060353.m2749.l2649&ssPageName=STRK%3AMEBIDX%3AIT) | | If no longer available from this source, you can order from Amazon, but then follow the instructions below for reversing the yellow and orange wires.
StarTech indictor LED (http://www.amazon.com/gp/product/B00213KDQK?psc=1&redirect=true&ref_=oh_aui_detailpage_o07_s00)
USB 2.0 8GB thumb drive (https://www.amazon.com/SanDisk-Cruzer-Low-Profile-Drive-SDCZ33-008G-B35/dp/B005FYNSUA) | | Or use your own USB memory stick, but it needs to be physically small as there isn’t much space in the wood case.
Female-female jumper wires (https://www.amazon.com/Phantom-YoYo-Dupont-Cable-Female/dp/B00KOL5BCC)
1ft male-male headphone cable (https://www.amazon.com/Auxiliary-Compatible-Smartphones-Tablets-Players/dp/B00LM0U8I6)
Panel mount headphone jack (http://www.amazon.com/gp/product/B004JX64FE?psc=1&redirect=true&ref_=oh_aui_detailpage_o03_s00)
Sticky back velcro (http://www.amazon.com/gp/product/B000TGSPV6?psc=1&redirect=true&ref_=oh_aui_search_detailpage) | | Or use the sticky back Velcro that you already have.
Elmer’s wood glue (http://www.amazon.com/Elmers-E7010-Carpenters-Wood-Ounces/dp/B0045PTHH8) | | Or use the wood glue you already have.
AmazonBasics Lightweight On-Ear Headphones (https://www.amazon.com/gp/product/B00NBEWB4U/ref=oh_aui_search_detailpage?ie=UTF8&psc=1) | | Or if the recipient already has familiar good headphones, use those instead. Or for $9 less, use these not-quite-as-nice Panasonics (https://www.amazon.com/gp/product/B00004T8R2/ref=oh_aui_search_detailpage?ie=UTF8&psc=1).

Check to see if your computer has an SD-card reader. If not, your spouse/child/friend probably has one. If not, you can order a USB SD-card reader (https://www.amazon.com/gp/product/B00OJ5WBUE/ref=oh_aui_search_detailpage?ie=UTF8&psc=1) for your computer.

Note that this project uses the built-in headphone jack on the Raspberry Pi. And it makes use of some new software from the Raspberry Pi Foundation that makes for excellent audio quality. Previous versions of this project used a USB audio adapter, but that’s not necessary any more.

# 8 Assemble the personalized collection of music

## 8.1 Choosing the music – go for familiar favorites

This is the most important step. The personalized (familiar) music is the fundamental magic. You don’t need much music, perhaps 6-10 albums. But only familiar favorites. One of the few benefits of dementia is that you don’t remember what you just listened to and thus don’t get tired of your favorite albums. In my case, my Mom mailed me my Dad’s favorite CDs. It will take two weeks for the parts above to arrive, so you have time to do this well.

## 8.2 Put the music on the USB memory stick

Organize the digitized music into folders on the USB memory stick, one folder per album. MP3, iTunes, and FLAC files are supported i.e. files with extensions .mp3, .m4a, .flac. In the end, you should have a set of folders that looks something like this:


# 9 Prepare the micro-SD memory card

I prepared a disk image for you. Your job is to download this disk image and then write it to the micro-SD card. The steps:

1. If you are using Windows, install Win32 Disk Imager (http://sourceforge.net/projects/win32diskimager/). This is what I use. If you are using a Mac, try Etcher (https://etcher.io/). Or try ApplePi-Baker (http://www.tweaking4all.com/software/macosx-software/macosx-apple-pi-baker/) (if a recent version e.g. v1.9.4 doesn’t work for you, try v1.5.1).
2. Download the DQMusicBox disk image (https://drive.google.com/file/d/0B1Q1o5gn_EfkaHNSQ0lJVjdYd2c/view). 449MB.


3. Unzip to extract dqmusicbox_2016_12_30.img.
4. Put the micro-SD memory card into the SD card adapter i.e. put the tiny card into the larger card.
5. Put the SD card adapter into the SD reader/writer in your computer.
6. Start the Win32 Disk Imager program, instruct it to write the image file to the SD card:


7. Wait for the writing to complete, ~10 minutes. This would be a good time to make a sandwich.

# 10 Put it all together

What you should end up with (with top removed):


I don’t think you need all the steps listed out. But here are a few tips for putting it all together:

1. Glue the bottom and sides of the wood case. Put the top on, but don’t glue it. Use painter’s tape or other to hold the box together while the glue dries.
2. Put the Raspberry Pi into the plastic case.
3. Insert the USB memory stick into a USB port on the Raspberry Pi.
4. Put the micro-SD memory card into the Raspberry Pi memory card slot.
5. Use Velcro to hold the plastic case (and its contents) in place in the wood case.
6. Mount the rotary encoders in the two medium-sized holes in front panel.
7. Mount the headphone jack in the large hole on the front panel.
8. Connect the headphone jack on the Pi to the headphone jack that you just installed in the case.
9. Find the indicator LED labeled HDD. Push this LED into the small hole in the front panel, it should fit snugly.
10. Mount the headphone jack connector in the large hole in the front panel.
11. Now add the wires:

You’ll start from the unused pins on the Pi, which are arranged in two rows of twenty pins:


Your goal is to make it look like this:


Use the wiring diagram below to make the right connections. Just push the jumper cables in place – no soldering unless you really want to.

Note: the various rotary encoder manufacturers don’t seem to agree on which pin indicates clockwise and which pin indicates counter-clockwise. If your music box is so reversed (e.g. if a clockwise turn *decreases* volume), then just change the orange & yellow wires on the rotary encoders:

  - For the volume knob rotary encoder:
    - Leave the orange wire on pin 9 on the Pi, but now connect the orange wire to the CLK pin on the rotary encoder.
    - Leave the yellow wire on pin 11 on the Pi, but now connect the yellow wire to the DT pin on the rotary encoder.
  - For the songs knob rotary encoder:
    - Leave the orange wire on pin 3 on the Pi, but now connect the orange wire to the CLK pin on the rotary encoder.
    - Leave the yellow wire on pin 4 on the Pi, but now connect the yellow wire to the DT pin on the rotary encoder.

# 11 Test cases

Now that you have assembled everything, it is time to test.

Test | Description & Expectation
Light 15sec after power on | The indicator LED turns on when DQMusicBox is ready to play music, which is generally about 15 seconds after power on.
Start song | Turning either of the knobs will start music playing.
Change song | Turn the songs knob. If you go forward and backward through the song list as expected, then all is well.
Change volume | Turn the volume knob. If the volume goes up and down as expected, then all is well.
Pause | Tap the volume knob, song should pause. Tap the songs knob, this should also pause the song.
Unpause | Tap a knob

# 12 Congratulations

Congratulations! You should have a fully functional DQMusicBox.

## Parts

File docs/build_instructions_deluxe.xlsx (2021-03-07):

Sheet: case_1
Item | Supplier | Cost | Notes & alternatives
Cherry case | Ponoko | $84.77 | See instructions above.
Raspberry Pi Zero WH (https://www.adafruit.com/product/3708) | Adafruit | $14.00 | Or buy PiShop.us SKU 1052
power supply: 5V 3A, micro-USB (https://www.adafruit.com/product/1995) | Adafruit | $7.50 | Or buy Amazon B00MARDJZ4
Premium Female/Female Jumper Wires - 40 x 6" (https://www.adafruit.com/product/266) | AdaFruit | $3.95 | Or buy Amazon B07GCY6CH7
USB hub HAT for Pi Zero (https://www.amazon.com/gp/product/B01IT1TLFQ/ref=oh_aui_detailpage_o01_s00?ie=UTF8&psc=1) | Amazon | $13.99 | Or search for "MakerSpot 4-Port Stackable USB Hub HAT"
USB DAC (https://www.amazon.com/gp/product/B00KGK5I38/ref=ox_sc_saved_title_3?smid=ATVPDKIKX0DER&psc=1) | Amazon | $22.99 | Or Amazon B00F7120TQ
M2.5 standoffs (spacing screws) (https://www.amazon.com/Sutemribor-Female-Spacer-Standoff-Assortment/dp/B075K3QBMX) | Amazon | $12.99
M2.5 screws length=10mm ThreadPitch=0.45 (https://www.amazon.com/Machine-Finish-Phillips-M2-5-0-45-Threaded/dp/B00F33S93E?rps=1) | Amazon | $7.31
16GB+ micro SD card (https://www.amazon.com/gp/product/B06XWN9Q99/ref=ppx_yo_dt_b_asin_title_o05_s00?ie=UTF8&psc=1) | Amazon | $7.49 | Or buy Amazon B06XWN9Q99 or other 16GB+ card
USB thumb drive (https://www.amazon.com/gp/product/B077Y149DL/ref=ppx_yo_dt_b_search_asin_title?ie=UTF8&psc=1) | Amazon | $7.19 | Or Amazon B07MDXBT87 or other physically small USB drive
Arvicka speakers (https://www.amazon.com/gp/product/B01KC7WGQQ/ref=oh_aui_search_detailpage?ie=UTF8&psc=1) | Amazon | $29.99 | Other speakers no larger than 56W x 56D x 66H mm per speaker & take 3.5mm audio jack input & USB power
Speaker cloth (https://www.amazon.com/gp/product/B01HMBKQNA/ref=oh_aui_search_detailpage?ie=UTF8&psc=1) | Amazon | $9.99
Light dimming stickers (https://www.amazon.com/dp/B00CLVEQCO/ref=dp_prsubs_3) | Amazon | $6.89 | Optional, but the status LED is really bright. Or use dark tape.
E6000 adhesive (https://www.amazon.com/E6000-Plus-570110-Adhesive-Clear/dp/B07QJDJYC6) | Amazon | $6.96 | Or buy at hobby store cheaper. If you have a crafting friend, they probably have some.
KY-040 rotary encoder knobs (https://www.amazon.com/Tegg-KY-040-Encoder-clickable-Arduino/dp/B07QL6V4WP) | Amazon | $7.99 | Or Amazon B06XQTHDRR
KY-016 indicator LED (https://www.banggood.com/5Pcs-KY-016-RGB-3-Color-LED-Module-Red-Green-Blue-p-954086.html?rmmds=search&cur_warehouse=CN) | Banggood | $4.61 | ALLOW 3+ WEEKS TO ARRIVE FROM CHINA. Due to COVID, it's hard to find these in the US. You can get it quickly from Amazon B07KJYR8K1, but costs $18.
TOTAL |  | $248.61 | Prices will vary. Does not include tax, shipping.

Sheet: case_10
# units to make | 10
Item | Supplier | Quan | Each | Total | Per unit | Notes
Cherry case |  | 10 | $25.00 | $250.00 | $25.00 | Or order 10+ from Ponoko for @$49.76
Raspberry Pi Zero WH (https://www.adafruit.com/product/3708) | Adafruit | 10 | $14.00 | $140.00 | $14.00
power supply: 5V 3A, micro-USB (https://www.adafruit.com/product/1995) | Adafruit | 10 | $7.50 | $75.00 | $7.50
USB hub HAT for Pi Zero (https://www.amazon.com/gp/product/B01IT1TLFQ/ref=oh_aui_detailpage_o01_s00?ie=UTF8&psc=1) | Amazon | 10 | $13.99 | $139.90 | $13.99
USB DAC (https://www.amazon.com/gp/product/B00KGK5I38/ref=ox_sc_saved_title_3?smid=ATVPDKIKX0DER&psc=1) | Amazon | 10 | $22.99 | $229.90 | $22.99
M2.5x6mm + 6mm standoffs (50 pieces) (https://www.aliexpress.com/item/32968818335.html) | Ali Express | 2 | $2.43 | $4.86 | $0.49
M2.5x15mm + 6mm standoffs (50 pieces) (https://www.aliexpress.com/item/32968818335.html) | Ali Express | 1 | $2.38 | $2.38 | $0.24
M2.5 screws length=10mm ThreadPitch=0.45 (https://www.amazon.com/Machine-Finish-Phillips-M2-5-0-45-Threaded/dp/B00F33S93E?rps=1) | Amazon | 1 | $7.31 | $7.31 | $0.73
16GB+ micro SD card (https://www.amazon.com/gp/product/B06XWN9Q99/ref=ppx_yo_dt_b_asin_title_o05_s00?ie=UTF8&psc=1) | Amazon | 10 | $7.49 | $74.90 | $7.49
USB thumb drive (https://www.amazon.com/gp/product/B077Y149DL/ref=ppx_yo_dt_b_search_asin_title?ie=UTF8&psc=1) | Amazon | 10 | $7.19 | $71.90 | $7.19
Arvicka speakers (https://www.amazon.com/gp/product/B01KC7WGQQ/ref=oh_aui_search_detailpage?ie=UTF8&psc=1) | Amazon | 10 | $29.99 | $299.90 | $29.99
Speaker cloth (large cloth) (https://www.amazon.com/gp/product/B01HMBKQNA/ref=oh_aui_search_detailpage?ie=UTF8&psc=1) | Amazon | 1 | $9.99 | $9.99 | $1.00
Light dimming stickers (https://www.amazon.com/dp/B00CLVEQCO/ref=dp_prsubs_3) | Amazon | 1 | $6.89 | $6.89 | $0.69
E6000 adhesive (https://www.amazon.com/E6000-Plus-570110-Adhesive-Clear/dp/B07QJDJYC6) | Amazon | 1 | $6.96 | $6.96 | $0.70
KY-040 rotary encoders (knobs) (https://www.aliexpress.com/item/599712551.html) | Ali Express | 20 | $0.72 | $11.00 | $1.10
Female-female jumper wires 30cm (https://www.aliexpress.com/item/32987024879.html) | Ali Express | 10 | $1.24 | $12.40 | $1.24
KY-016 indicator LED (10 pieces) (https://www.aliexpress.com/item/32955003054.html?spm=a2g0s.9042311.0.0.6b164c4d50jzDO) | Ali Express | 1 | $1.92 | $1.92 | $0.19
Sticky back rubber feet (100 pieces) (https://www.aliexpress.com/item/4000157727846.html) | Ali Express | 1 | $1.09 | $1.09 | $0.11 | Only needed for wood < 6mm thick
 |  |  |  |  | $134.63 | +tax + shipping

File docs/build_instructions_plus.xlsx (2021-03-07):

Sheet: parts_1
Item | Supplier | Cost | Notes & alternatives
Case | Ponoko | $69.98 | See instructions above
Raspberry Pi 4 Model B - 2GB RAM (https://www.adafruit.com/product/4292) | AdaFruit | $35.00 | Or buy Amazon B07TD42S27 (Pi 4). Or buy a Pi 3B+ and the appropriate power supply (not the Pi 4 power supply below).
Premium Female/Female Jumper Wires - 40 x 6" (https://www.adafruit.com/product/266) | AdaFruit | $3.95 | Or buy Amazon B07GCY6CH7
Official Raspberry Pi 4 Power Supply 5.1V 3A with USB C (https://www.adafruit.com/product/4298) | AdaFruit | $7.95 | Or buy Amazon B07TYQRXTK
Panel Mount USB Cable - A Male to A Female (https://www.adafruit.com/product/908) | AdaFruit | $3.95 | Or buy Amazon B0718XQPGB. Amazon B07C87FYLY *may* work, but you'll also need to buy M3 screws.
M2.5 standoffs (spacing screws) (https://www.amazon.com/Sutemribor-Female-Spacer-Standoff-Assortment/dp/B075K3QBMX) | Amazon | $12.99 | Or buy Amazon B075K3QBMX
M2.5 screws 12mm M2.5-0.45 (https://www.amazon.com/gp/product/B000NHXOW6/ref=ppx_yo_dt_b_asin_title_o02_s00?ie=UTF8&psc=1) | Amazon | $6.85 | You can probably also buy these at a good hardware store for less
Speaker cloth (brown, large piece) (https://www.amazon.com/ZUINIUBI-Speaker-Cloth-Stereo-Fabric/dp/B01HMBKQNA?swrs=19F44B4F21A0841A381DCAC901FC0468) | Amazon | $9.99 | Or buy Amazon B01HMBKNSS (black, large cloth)
Speakers (https://www.amazon.com/gp/product/B06XDSMDKV/ref=ppx_yo_dt_b_asin_title_o03_s00?ie=UTF8&psc=1) | Amazon | $9.99 | Or buy Amazon B01KC7WGQQ
16GB+ micro SD card (https://www.amazon.com/gp/product/B06XWN9Q99/ref=ppx_yo_dt_b_asin_title_o05_s00?ie=UTF8&psc=1) | Amazon | $7.49 | Or buy Amazon B06XWN9Q99 or other 16GB+ card
USB thumb drive (https://www.amazon.com/gp/product/B077Y149DL/ref=ppx_yo_dt_b_search_asin_title?ie=UTF8&psc=1) | Amazon | $7.19 | Or Amazon B07MDXBT87 or other physically small USB drive
KY-016 indicator LED (https://www.banggood.com/5Pcs-KY-016-RGB-3-Color-LED-Module-Red-Green-Blue-p-954086.html?rmmds=search&cur_warehouse=CN) | Banggood | $4.61 | ALLOW ~3 WEEKS TO ARRIVE FROM CHINA. Due to COVID, it's hard to find these in the US. You can get it quickly from Amazon B07KJYR8K1, but costs $18.
KY-040 rotary encoders (knobs) (https://www.amazon.com/Tegg-KY-040-Encoder-clickable-Arduino/dp/B07QL6V4WP) | Amazon | $7.99 | Or buy Amazon B06XQTHDRR
Sticky back velcro strips (https://www.amazon.com/VELCRO-Brand-Fasteners-Perfect-General/dp/B000TGSPV6) | Amazon | $2.98 | Or buy Amazon B0035GZCHC
TOTAL |  | $190.91 | + tax + shipping

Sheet: parts_10
# units to make | 10
Item | Supplier | Quan | Each | Total | Per unit | Notes
Wood case | Maker space | 10 | $21.50 | $215.00 | $21.50 | Or order 10+ from Ponoko for @$46.53
Raspberry Pi 4 Model B - 2GB RAM (https://www.adafruit.com/product/4292) | AdaFruit | 10 | $35.00 | $350.00 | $35.00
Official Raspberry Pi Power Supply 5.1V 3A with USB C - 1.5 meter long (https://www.adafruit.com/product/4298) | AdaFruit | 10 | $7.95 | $79.50 | $7.95
Panel Mount USB Cable - A Male to A Female (https://www.adafruit.com/product/908) | AdaFruit | 10 | $3.95 | $39.50 | $3.95
Female-female jumper wires 30cm (https://www.aliexpress.com/item/32987024879.html) | Ali Express | 10 | $1.24 | $12.40 | $1.24
M2.5x6mm + 6mm standoffs (50 pieces) (https://www.aliexpress.com/item/32968818335.html) | Ali Express | 1 | $2.38 | $2.38 | $0.24
M2.5x15mm + 6mm standoffs (50 pieces) (https://www.aliexpress.com/item/32968818335.html) | Ali Express | 1 | $3.41 | $3.41 | $0.34
M2.5x20mm + 6mm standoffs (50 pieces) (https://www.aliexpress.com/item/32968818335.html) | Ali Express | 1 | $3.95 | $3.95 | $0.40
M2.5 screws 12mm M2.5-0.45 (100 pieces) (https://www.amazon.com/gp/product/B000NHXOW6/ref=ppx_yo_dt_b_asin_title_o02_s00?ie=UTF8&psc=1) | Amazon | 1 | $6.85 | $6.85 | $0.68
Speaker cloth (large cloth) (https://www.amazon.com/ZUINIUBI-Speaker-Cloth-Stereo-Fabric/dp/B01HMBKQNA) | Amazon | 1 | $9.99 | $9.99 | $1.00
Speakers (https://www.amazon.com/gp/product/B06XDSMDKV/ref=ppx_yo_dt_b_asin_title_o03_s00?ie=UTF8&psc=1) | Amazon | 10 | $9.99 | $99.90 | $9.99
Micro SD card (https://www.amazon.com/gp/product/B06XWN9Q99/ref=ppx_yo_dt_b_asin_title_o05_s00?ie=UTF8&psc=1) | Amazon | 10 | $7.49 | $74.90 | $7.49
USB flash drive (https://www.amazon.com/dp/B077Y149DL/ref=psdc_3151491_t3_B005FYNSUA) | Amazon | 10 | $7.19 | $71.90 | $7.19
KY-040 rotary encoders (knobs) (https://www.aliexpress.com/item/599712551.html) | Ali Express | 20 | $0.72 | $14.40 | $1.44
KY-016 indicator LED (10 pieces) (https://www.aliexpress.com/item/32955003054.html?spm=a2g0s.9042311.0.0.6b164c4d50jzDO) | Ali Express | 1 | $1.92 | $1.92 | $0.19
Sticky back velcro strips (5 yards) (https://www.amazon.com/Strenco-Inch-Self-Adhesive-Hook/dp/B00FQ937NM) | Amazon | 1 | $7.92 | $7.92 | $0.79
Sticky back rubber feet (100 pieces) (https://www.aliexpress.com/item/4000157727846.html) | Ali Express | 1 | $1.09 | $1.09 | $0.11 | Only needed for wood < 6mm thick
TOTAL |  |  |  |  | $99.50 | + tax + shipping

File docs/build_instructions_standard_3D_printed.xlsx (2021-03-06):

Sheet: case_1
Item | Supplier | Cost | Notes & alternatives
Raspberry Pi 1 A+ single board computer (http://www.newark.com/raspberry-pi/raspbrry-moda-512m/silicon-manufacturer-broadcom/dp/81Y5333) | Newark | $20.00 | Also tested with a 2B, 3A+, 3B, 3B+, 4B. Do not use Pi Zero.
Power supply (https://www.newark.com/pro-elec/28-19339/adaptor-ac-dc-5-1v-2-5a/dp/51AC7144) | Newark | $4.99 | Or Newark 81AC2845. Or order one for your region/plug.
Female-female jumper wires (http://www.newark.com/adafruit/266/female-to-female-jumper-wires/dp/42X1200) | Newark | $3.95 | Or Amazon B01L5ULRUA
Panel mount 3.5mm headphone jack (http://www.newark.com/mcm/27-5937/3-5mm-inline-stereo-mount-female/dp/40T6284) | Newark | $2.69 | Or Amazon B004JX64FE
M2.5 standoffs (screws) – 8 of them (https://www.newark.com/raf-electronic-hardware/m2102-2545-al/spacer-standoff-hex-aluminium/dp/27T7975?st=M2.5%20standoff) | Newark | $7.12 | Or Amazon B06XXV8RTR
16GB+ micro SD card (https://www.amazon.com/gp/product/B06XWN9Q99/ref=ppx_yo_dt_b_asin_title_o05_s00?ie=UTF8&psc=1) | Amazon | $4.95 | Or buy Amazon B06XWN9Q99 or other 16GB+ card
USB thumb drive (https://www.amazon.com/gp/product/B077Y149DL/ref=ppx_yo_dt_b_search_asin_title?ie=UTF8&psc=1) | Amazon | $7.19 | Or Amazon B07MDXBT87 or other physically small USB drive
Audio cable (https://www.amazon.com/gp/product/B00LM0U8I6/ref=oh_aui_detailpage_o00_s00?ie=UTF8&psc=1) | Amazon | $6.59 | Or Amazon B00SUIKMJ8 or audio cable with right angle bend
KY-016 indicator LED (https://www.banggood.com/5Pcs-KY-016-RGB-3-Color-LED-Module-Red-Green-Blue-p-954086.html?rmmds=search&cur_warehouse=CN) | Banggood | $4.61 | ALLOW 3+ WEEKS TO ARRIVE FROM CHINA. Due to COVID, it's hard to find these in the US. You can get it quickly from Amazon B07KJYR8K1, but costs $18.
KY-040 rotary encoders (knobs) (https://www.amazon.com/Tegg-KY-040-Encoder-clickable-Arduino/dp/B07QL6V4WP) | Amazon | $7.99 | Or Amazon B06XQTHDRR.
#4 x 5/8” flat head wood screws (https://www.amazon.com/Snug-Fastener-Stainless-Phillips-SNG107/dp/B07L4B9DHY) | Amazon | $7.30 | Or buy at your local hardware store for less
 |  | $77.38 | Prices will vary. Does not include tax, shipping.

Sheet: case_10
# units to make | 10
Item | Supplier | Quan | Each | Total | Per unit | Notes
Raspberry Pi 1 A+ single board computer (http://www.newark.com/raspberry-pi/raspbrry-moda-512m/silicon-manufacturer-broadcom/dp/81Y5333) | Newark | 10 | $20.00 | $200.00 | $20.00
Power supply (https://www.newark.com/pro-elec/28-19339/adaptor-ac-dc-5-1v-2-5a/dp/51AC7144) | Newark | 10 | $4.99 | $49.90 | $4.99
Panel mount 3.5mm headphone jack (http://www.newark.com/mcm/27-5937/3-5mm-inline-stereo-mount-female/dp/40T6284) | Newark | 10 | $2.69 | $26.90 | $2.69
Female-female jumper wires (https://www.aliexpress.com/item/32800215149.html?spm=a2g0s.9042311.0.0.6b164c4d50jzDO) | Ali Express | 10 | $0.60 | $6.00 | $0.60
M2.5 6mm thread + 6mm standoff screws (100 pieces) (https://www.aliexpress.com/item/32789600225.html?spm=a2g0s.9042311.0.0.27424c4dxaP132) | Ali Express | 1 | $1.98 | $1.98 | $0.20
Audio cable (https://www.aliexpress.com/item/32828101917.html?spm=a2g0s.9042311.0.0.6b164c4d50jzDO) | Ali Express | 10 | $2.79 | $27.90 | $2.79
KY-016 indicator LED (10 pieces) (https://www.aliexpress.com/item/32955003054.html?spm=a2g0s.9042311.0.0.6b164c4d50jzDO) | Ali Express | 1 | $1.92 | $1.92 | $0.19
KY-040 rotary encoders (knobs) (https://www.aliexpress.com/item/599712551.html) | Ali Express | 20 | $0.72 | $14.40 | $1.44
16GB+ micro SD card (https://www.amazon.com/gp/product/B06XWN9Q99/ref=ppx_yo_dt_b_asin_title_o05_s00?ie=UTF8&psc=1) | Amazon | 10 | $7.48 | $74.80 | $7.48
USB thumb drive (https://www.amazon.com/gp/product/B077Y149DL/ref=ppx_yo_dt_b_search_asin_title?ie=UTF8&psc=1) | Amazon | 10 | $7.19 | $71.90 | $7.19
#4 x 5/8” flat head wood screws (100 pieces) (https://www.amazon.com/Snug-Fastener-Stainless-Phillips-SNG107/dp/B07L4B9DHY) | Amazon | 1 | $7.30 | $7.30 | $0.73
 |  |  |  |  | $48.30 | + tax + shipping

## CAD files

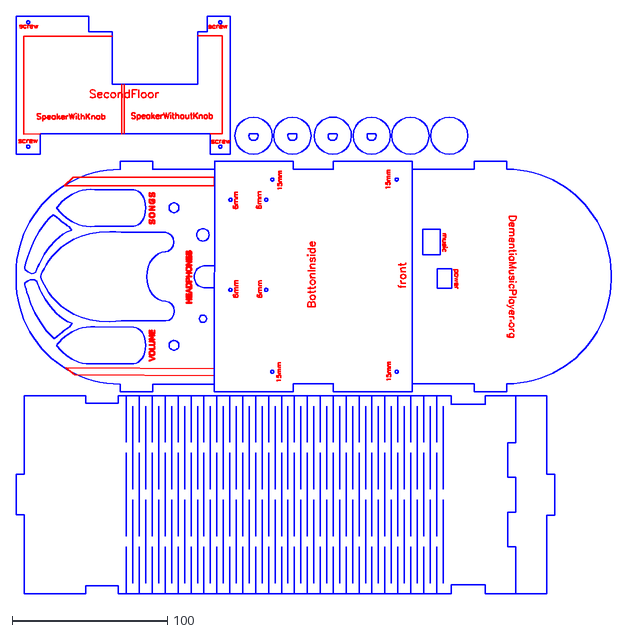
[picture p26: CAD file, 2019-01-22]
case/deluxe_model/DementiaFriendlyMusicPlayer_Deluxe_5point2mm.dxf
383.1 x 372.0

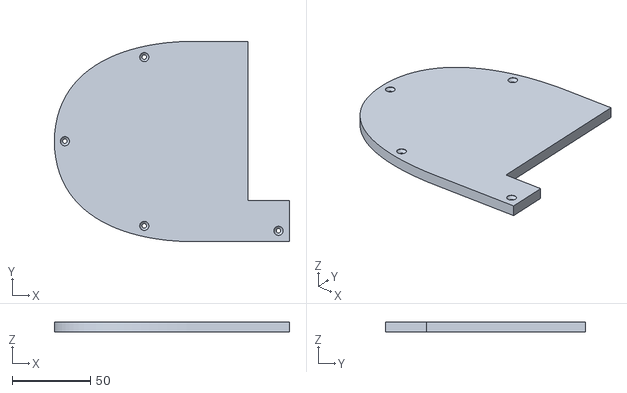
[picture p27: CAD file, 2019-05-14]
case/standard_model_3D_printed/Back.stl
150.0 x 128.0 x 6.70

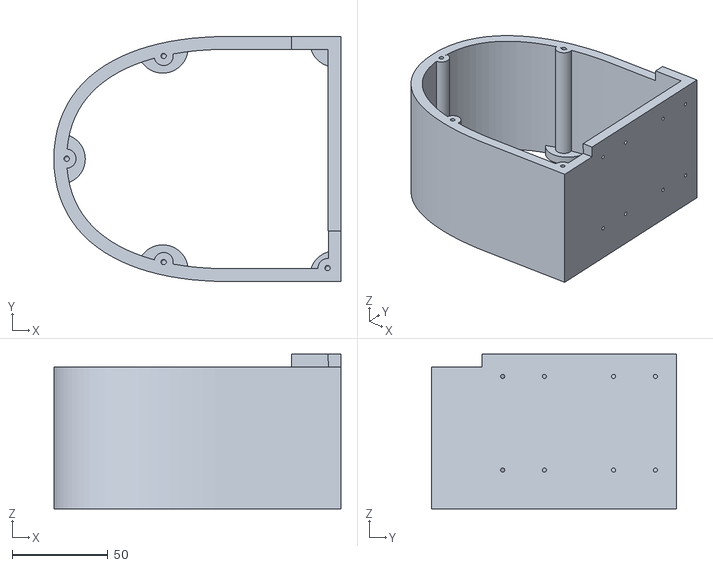
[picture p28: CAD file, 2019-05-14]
case/standard_model_3D_printed/Body.stl
150.0 x 128.0 x 81.0

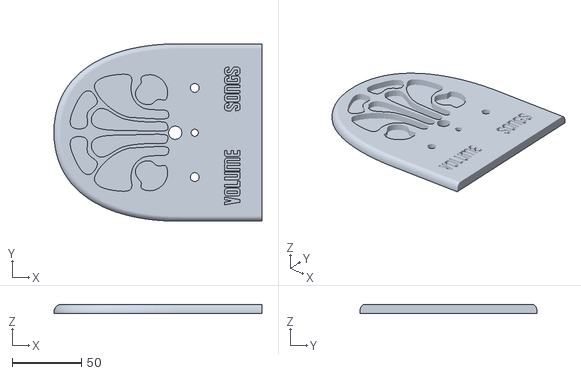
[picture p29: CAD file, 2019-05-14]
case/standard_model_3D_printed/Front.stl
150.0 x 128.0 x 6.70

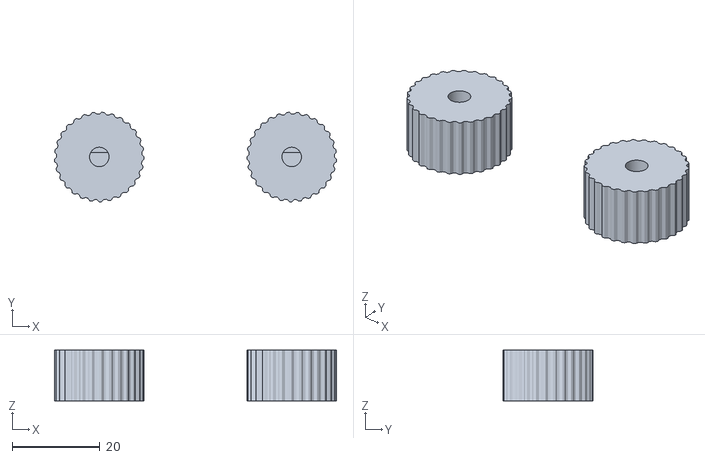
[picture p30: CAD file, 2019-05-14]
case/standard_model_3D_printed/Dials.stl
64.1 x 20.4 x 11.6

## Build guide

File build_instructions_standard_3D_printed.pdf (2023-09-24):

1

# How to Build the Dementia Friendly Music Player - 3D Printed Case

# Standard Model - 3D Printed: Use with Headphones or External Speakers

24 September 2023, http://DementiaMusicPlayer.org, Ross Porter rosswesleyporter@gmail.com

I was inspired to design this by the documentary Alive Inside (http://www.aliveinside.us/#land) which shows the profound joy felt by some with dementia when listening to their favorite music.

### My Dad could no longer operate the home stereo. But he could operate this music player because it operates like a familiar two-knob radio. The vintage style fit with his old intact memories – for most people with dementia, the old

memories are the strong memories.

### It’s easier than you think to make one. Everything I did is open source. This document contains all the information you need. You can order the parts online, including the cut & engraved wood. It’s a good family project – kids do

well with this. It’s also a project that friends would love to help you with.

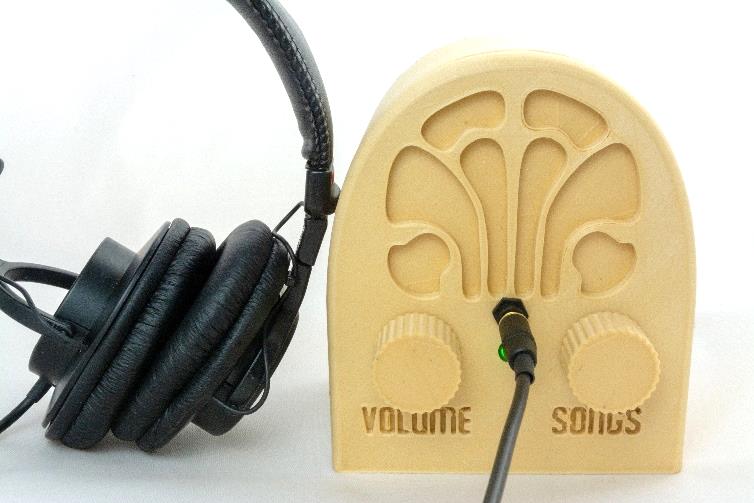
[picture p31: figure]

3D printed case designed by Trey Bagley

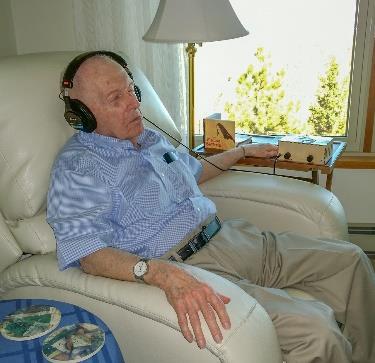
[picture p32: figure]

Parts cost | ~$80 + tax + shipping (drops to ~@$48 if make 10+ at a time, see Appendix 1)
Music cost | Minimal as you should use the recipient’s existing music collection
Build time | About 3 hours once you have the parts & music, Best if those 3 hours are spread across two days
Parts source | All parts can be mail ordered, links below
Soldering? | No
3D printer needed? | Yes, or work with a friend that has a 3D printer
3D printing time | About 18 hours
With a friend? | Good idea, especially if your friend has the basic tools required
Beverage? | I recommend a hoppy IPA while you are assembling

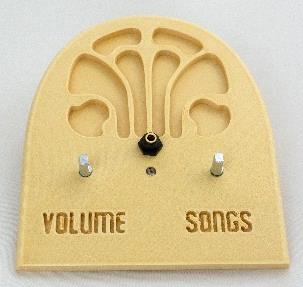
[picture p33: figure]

2

## Preview of the build steps

1) Order parts | 2) 3D print pieces | 3) Stain the pieces (optional)
4) Assemble recipient’s favorite music | 5) Copy software to micro SD card | 6) Collect the parts & pieces

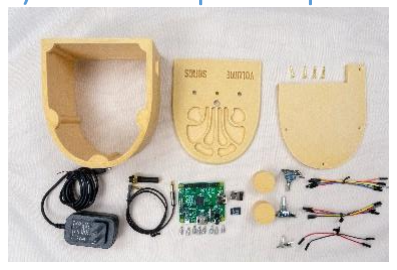
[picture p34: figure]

7) Add Pi | 8) Install front panel components | 9) Glue it

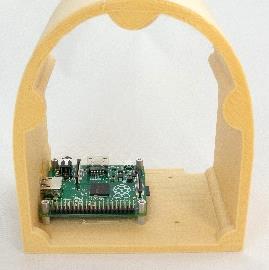
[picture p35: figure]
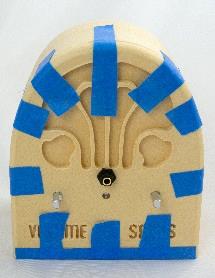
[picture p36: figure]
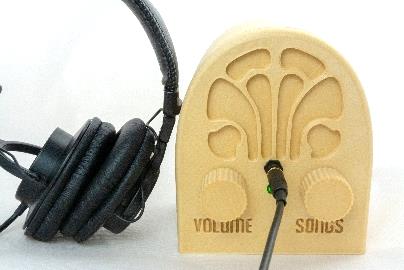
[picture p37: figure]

10) Wire it | 11) Screw on back | 12) Enjoy!

3

## No warranty

USE THESE DEMENTIA FRIENDLY MUSIC PLAYER PLANS AND SYSTEM AT YOUR OWN RISK. THE DEMENTIA FRIENDLY MUSIC PLAYER PLANS ARE PROVIDED AS IS WITHOUT WARRANTY OF ANY KIND EITHER EXPRESSED OR IMPLIED, INCLUDING, BUT NOT LIMITED TO, THE IMPLIED WARRANTIES OF MERCHANTABILITY AND FITNESS FOR A PARTICULAR PURPOSE. THE ENTIRE RISK AS TO THE QUALITY AND PERFORMANCE OF THE PLANS AND SYSTEM IS WITH YOU. SHOULD THE PLANS OR SYSTEM PROVE DEFECTIVE, YOU ASSUME THE COST OF ALL NECESSARY SERVICING, REPAIR OR CORRECTION. IN NO EVENT WILL ANY PARTY BE LIABLE TO YOU FOR DAMAGES, INCLUDING ANY GENERAL, SPECIAL, INCIDENTAL OR CONSEQUENTIAL DAMAGES ARISING OUT OF THE USE OR INABILITY TO USE THE PLANS OR SYSTEM.

## Acknowledgements

People were very generous with their time, and I really enjoyed the experience. This is certainly an incomplete list: Trey Bagley, Alex & Mike & others at Ada’s, (http://blog.seattletechnicalbooks.com/) the super helpful crew at Seattle Makers, (https://seattlemakers.org/) neighbor Randy, Stephen Christopher Phillips, (http://scphillips.com/) Bob Rathbone, (http://www.bobrathbone.com/) Stephen Rusk, (http://www.stephenrusk.com/) Graham Hill, (http://www.ted.com/speakers/graham_hill) support at Ponoko, (https://www.ponoko.com/) and my son.

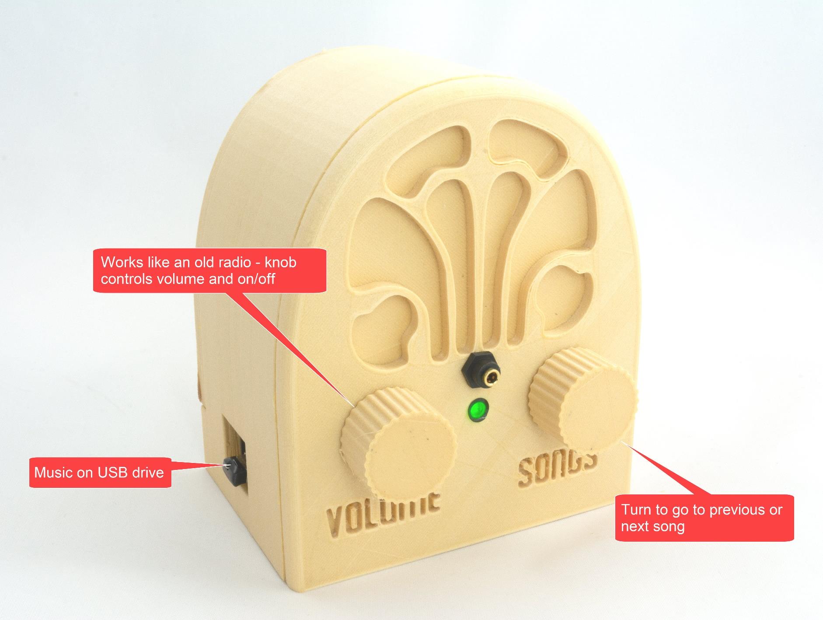
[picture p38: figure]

4

## How it works

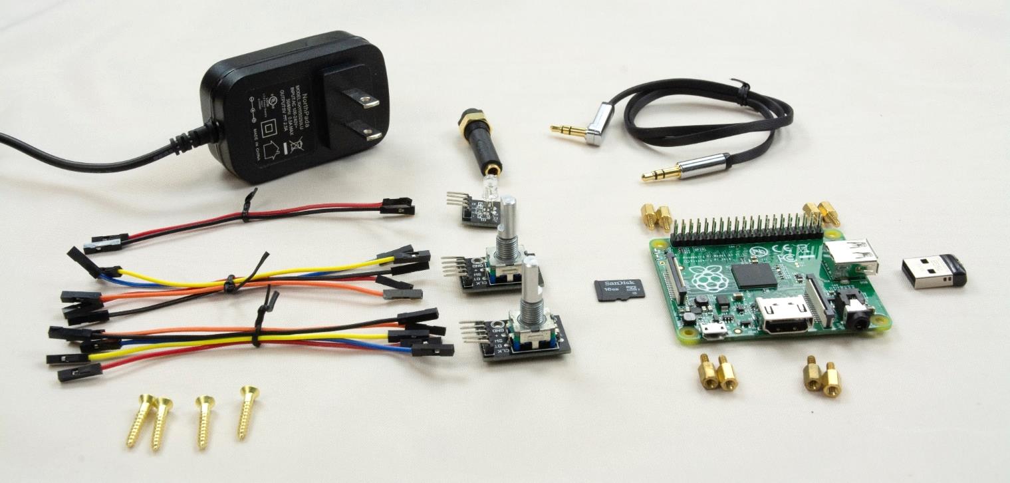
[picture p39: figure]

5

# STEP 1: Order the parts

If you plan to make 10+ units, see Appendix 1.

Item | Supplier | Cost | Notes & alternatives
Raspberry Pi 1 A+ single board computer (http://www.newark.com/raspberry-pi/raspbrry-moda-512m/silicon-manufacturer-broadcom/dp/81Y5333) | Newark | $20.00 | Also tested with a 2B, 3A+, 3B, 3B+, 4B. Do not use Pi Zero.
Power supply (https://www.newark.com/pro-elec/28-19339/adaptor-ac-dc-5-1v-2-5a/dp/51AC7144) | Newark | $4.99 | Or Newark 81AC2845. Or order one for your region/plug.
Female-female jumper wires (http://www.newark.com/adafruit/266/female-to-female-jumper-wires/dp/42X1200) | Newark | $3.95 | Or Amazon B01L5ULRUA
Panel mount 3.5mm headphone jack (http://www.newark.com/mcm/27-5937/3-5mm-inline-stereo-mount-female/dp/40T6284) | Newark | $2.69 | Or Amazon B004JX64FE
M2.5 standoffs (screws) – 8 of them (https://www.newark.com/raf-electronic-hardware/m2102-2545-al/spacer-standoff-hex-aluminium/dp/27T7975?st=M2.5%20standoff) | Newark | $7.12 | Or Amazon B06XXV8RTR
16GB+ micro SD card (https://www.amazon.com/gp/product/B06XWN9Q99/ref=ppx_yo_dt_b_asin_title_o05_s00?ie=UTF8&psc=1) | Amazon | $4.95 | Or buy Amazon B06XWN9Q99 or other 16GB+ card
USB thumb drive (https://www.amazon.com/gp/product/B077Y149DL/ref=ppx_yo_dt_b_search_asin_title?ie=UTF8&psc=1) | Amazon | $7.19 | Or Amazon B07MDXBT87 or other physically small USB drive
Audio cable (https://www.amazon.com/gp/product/B00LM0U8I6/ref=oh_aui_detailpage_o00_s00?ie=UTF8&psc=1) | Amazon | $6.59 | Or Amazon B00SUIKMJ8 or audio cable with right angle bend
KY-016 indicator LED (https://www.banggood.com/5Pcs-KY-016-RGB-3-Color-LED-Module-Red-Green-Blue-p-954086.html?rmmds=search&cur_warehouse=CN) | Banggood | $4.61 | ALLOW 3+ WEEKS TO ARRIVE FROM CHINA. Due to COVID, it's hard to find these in the US. You can get it quickly from Amazon B07KJYR8K1, but costs $18.
KY-040 rotary encoders (knobs) (https://www.amazon.com/Tegg-KY-040-Encoder-clickable-Arduino/dp/B07QL6V4WP) | Amazon | $7.99 | Or Amazon B06XQTHDRR.
#4 x 5/8” flat head wood screws (https://www.amazon.com/Snug-Fastener-Stainless-Phillips-SNG107/dp/B07L4B9DHY) | Amazon | $7.30 | Or buy at your local hardware store for less

| | $77.38 | Prices will vary. Does not include tax, shipping.

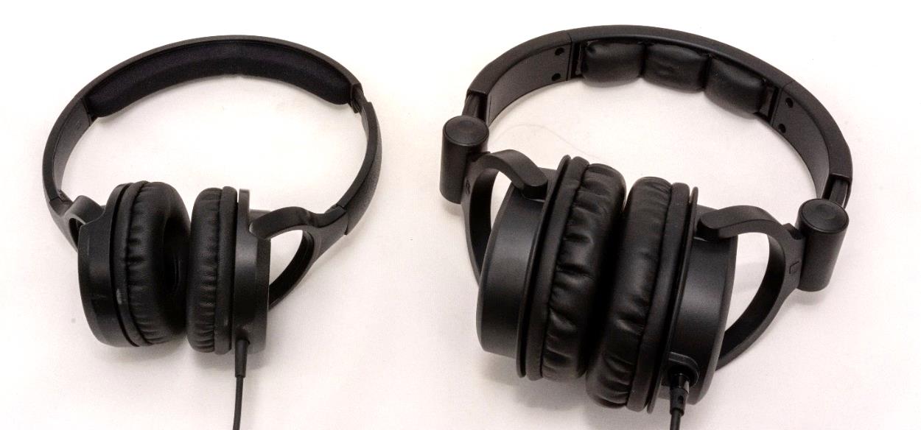
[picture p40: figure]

6

# STEP 2: Get Headphones

Item | Cost | Notes and alternatives
The recipient’s existing headphone | $0.00 | The best headphones are the headphones that the recipient is already used to.
Monoprice On-Ear headphones (https://www.monoprice.com/product?c_id=120&cp_id=12001&cs_id=1082302&p_id=13191&seq=1&format=2) | $10.99 | Very good sound. High sensitivity (which is important). Also available from Amazon for a slightly higher price but with Prime shipping: B014399CWK. (https://www.amazon.com/Monoprice-Lightweight-Headphones-Controls-Microphone/dp/B014399CWK)
Monoprice Over-the-Ear headphones (https://www.monoprice.com/product?c_id=120&cp_id=12001&cs_id=1082302&p_id=8323&seq=1&format=2) | $15.99 | Amazing sound. High sensitivity (which is important). Also available from Amazon for a slightly higher price but with Prime shipping: B007SP2CO2. (https://www.amazon.com/Monoprice-Headphones-Single-Button-Microphone-Controller/dp/B007SP2CO2)
Other | | Look for high sensitivity headphones, as the Pi’s output is a bit weak.

7

# STEP 3: Gather tools & supplies

You probably have some of these tools & supplies. If you don’t, you have a spouse or child or friend that does. This project is exactly the sort of thing that a friend would be happy to help you with.

Link to order item | Notes & alternatives
Elmer’s wood glue | Any wood glue will do
3/16th wrench or nut driver | Or needle-nosed pliers. Or really strong fingers
SD card reader/writer | Your computer may have an SD card reader/writer. If not, you probably have a friend that does. Or order a USB SD-card reader (https://www.amazon.com/gp/product/B00OJ5WBUE/ref=oh_aui_search_detailpage?ie=UTF8&psc=1) for your computer.
Painter’s tape | Any tape that comes off easily will do. Painter’s tape is great. Regular masking tape is probably fine too. I haven’t tried Scotch tape.
Light blocking tape or sticker | The unit’s LED is quite bright, so I prefer to block some of the light. You can use the tape above. Or order light blocking stickers such as B009WSJNCW. (https://www.amazon.com/LightDims-Original-Strength-Electronics-Appliances/dp/B009WSJNCW?s=hi)
PLA wood filament (optional) | This document assumes that you have a 3D printer, or you have a friend with a 3D printer. So you already have some regular PLA filament. I chose to use a PLA wood filament, specifically Monoprice PLA wood filament. (https://www.monoprice.com/product?p_id=12507)
Wood stain (optional) | If you print with PLA wood filament, you can optionally apply wood stain. I used a pre-stain, a stain, and a protective finish. I went to the local hardware store and purchased what they recommended: Minwax Pre-Stain Wood Conditioner, (https://www.minwax.com/wood-products/preparation/minwax-prestain-wood-conditioner) Minwax Wood Finish Cherry. (https://www.minwax.com/wood-products/stains/minwax-wood-finish#colors)

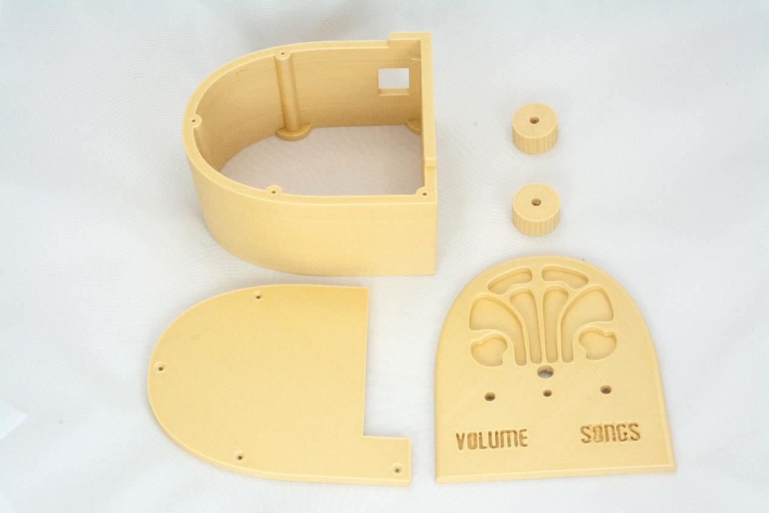
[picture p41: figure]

8

# STEP 4: 3D print the pieces

The key assumption is that you have a 3D printer, or you have a friend with a 3D printer. Thus, this document is not intended as an introduction to 3D printing.

You will be printing the pieces that you see below. You should print in the orientation that you see below i.e. flat side down. On my basic 3D printer, the total print time was about 18 hours.

3D printed case designed by Trey Bagley

## General instructions

1. Download the stl files (or (https://drive.google.com/drive/u/0/folders/1jW1gNMHsddQB-UOB9c4O4eo1X8JAw4f5) go to github (https://github.com/rosswesleyporter/dqmusicbox/) and clone the whole project)
2. 3D print the files.

## My experience

Trey Bagley designed the case. I think he did a great job. But I’m a novice at 3D printing. Nonetheless here is what I did, and I’m happy with the result:

9

- Monoprice Maker Select v2 3D printer (https://www.monoprice.com/product?p_id=13860)
- Monoprice PLA wood filament (https://www.monoprice.com/product?p_id=12507)
- Cura slicing software (https://ultimaker.com/en/products/ultimaker-cura-software)
- Key settings
- Layer height: 0.3mm
- Initial layer height: 0.3mm
- Wall thickness: 0.8mm
- Top/bottom thickness: 0.8mm
- Infill: 10%
- Print temp: 188C (this low temperature reduced stringing issues)
- Build plate temp: 50C
- Diameter: 1.75mm
- Flow: 100%
- Enable retraction: yes
- Retraction distance: 10mm
- Retraction speed: 60mm/sec
- Print speed: 45mm/sec
- Infill speed: 50mm/sec
- Travel speed: 120mm/sec
- Initial layer speed: 5mm/sec
- Enable print cooling: yes
- Fan speed: 100%
- Minimum layer time: 5 sec
- Print sequence: all at once
- Post printing
- My prints came out fairly clean, but I did use a tiny knife to extract extraneous strands from the lettering.

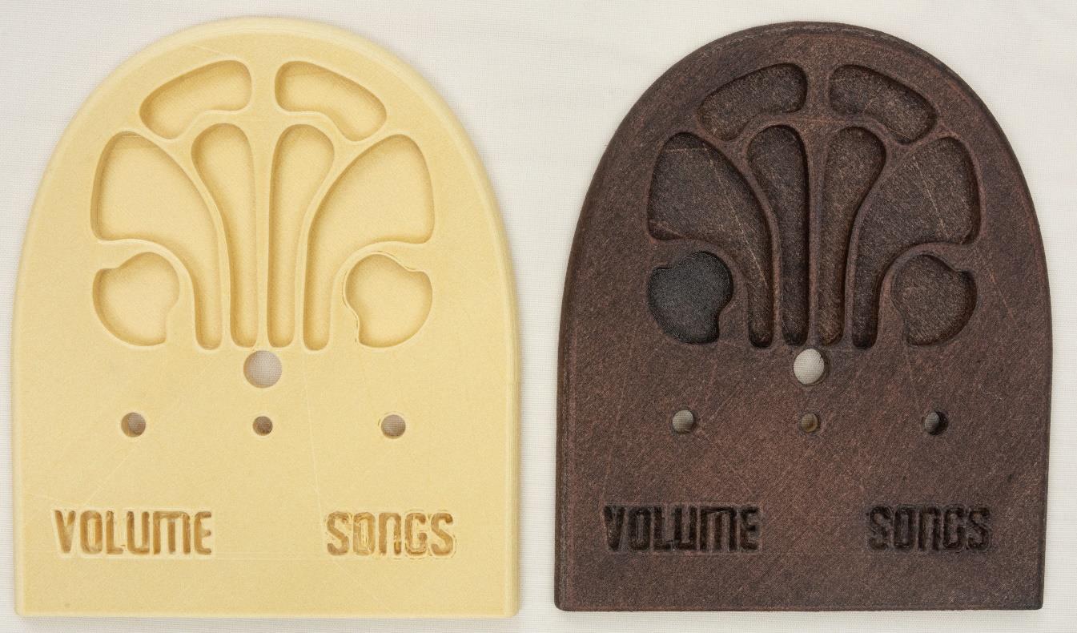
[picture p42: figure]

10

# STEP 5: Stain the pieces (optional)

This step is optional. I wanted to make something that seems familiar to someone with dementia i.e. make something that looks very much like a radio from the 1930s. These antique radios are made of wood and generally dark stained. Thus, I chose to print with a wood PLA filament and stain the print. You could choose to print with regular PLA filament. Or print with wood PLA but not stain it.

Here is the before and after of staining the front face:

I’m not a woodworker. Nonetheless, this is the process that I used:

1. Sand the parts with a fine grit sandpaper.
2. Apply Minwax Pre-Stain Wood Conditioner, (https://www.minwax.com/wood-products/preparation/minwax-prestain-wood-conditioner) let dry. Or a similar product. Minwax is what my neighborhood hardware store has…
3. Apply Minwax Wood Finish, Cherry. (https://www.minwax.com/wood-products/stains/minwax-wood-finish#colors) I applied a thin even coat. Minwax suggests waiting 15 minutes then wiping off the excess stain. I found this removed too much of the stain. So I didn’t do any wiping off and just let it dry overnight. The photo above is with a Minwax red mahogany stain, which I found a bit too dark – thus the cherry stain suggestion.

11

# STEP 6: Assemble the personalized collection of music

## Choosing the music – go for familiar favorites

This is the most important step. The personalized (familiar) music is the fundamental magic. You don’t need much music, perhaps 6-10 albums. But only familiar favorites. In my case, my Mom mailed me my Dad’s favorite CDs. It will take two weeks for the parts above to arrive, so you have time to do this well. Though it is easy to change the set of music later.

## Put the music on the USB memory stick

Organize the digitized music into folders on the USB memory stick, one folder per album. MP3, iTunes, and FLAC files are supported i.e. files with extensions .mp3, .m4a, .flac. In the end, you should have a set of folders that looks something like this:

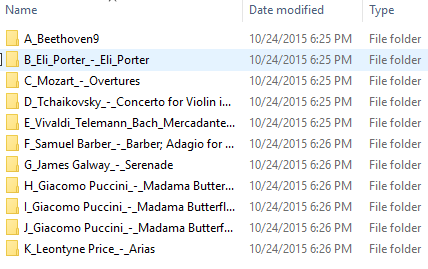
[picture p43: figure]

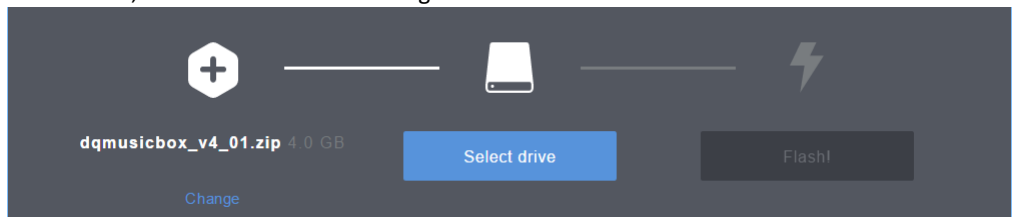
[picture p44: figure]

12

# STEP 7: Prepare the micro SD card

I prepared a disk image for you. It has all the required software. Your job is to download this disk image and then write it to the micro-SD card. The steps:

1. Install Etcher (https://etcher.io/) on your PC or Mac or Linux computer. Win32 Disk Imager (http://sourceforge.net/projects/win32diskimager/) also works.
2. Download the Dementia Friendly Music Player disk image. (https://drive.google.com/file/d/1T8aDpwgnpj7j2drFFBOlOxfJ5G6ao02I/view)
3. Confirm download – “Download anyway”
4. Put the micro-SD memory card into the SD card adapter that it came with i.e. put the tiny card into the larger card.
5. Put the SD card adapter into the SD reader/writer in your computer.
6. Start Etcher, instruct it to write the image file to the SD card:
7. Wait for the writing to complete, ~10 minutes. This would be a good time to make a sandwich.

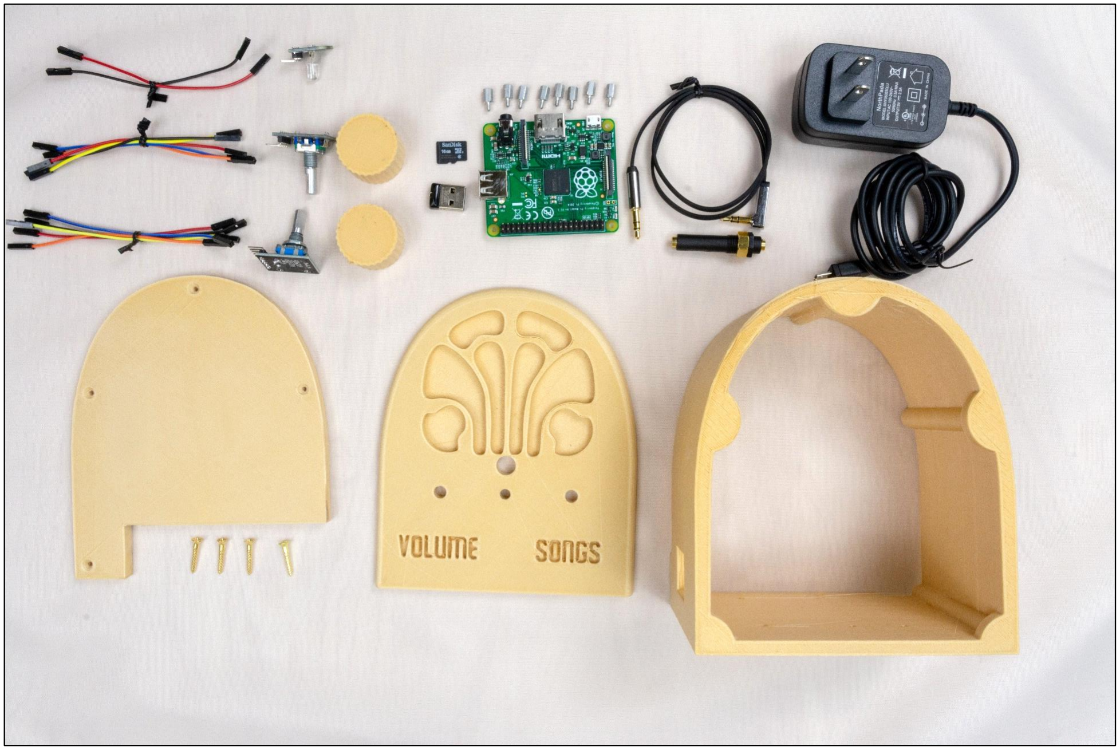
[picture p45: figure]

13

# STEP 8: Collect the parts & pieces

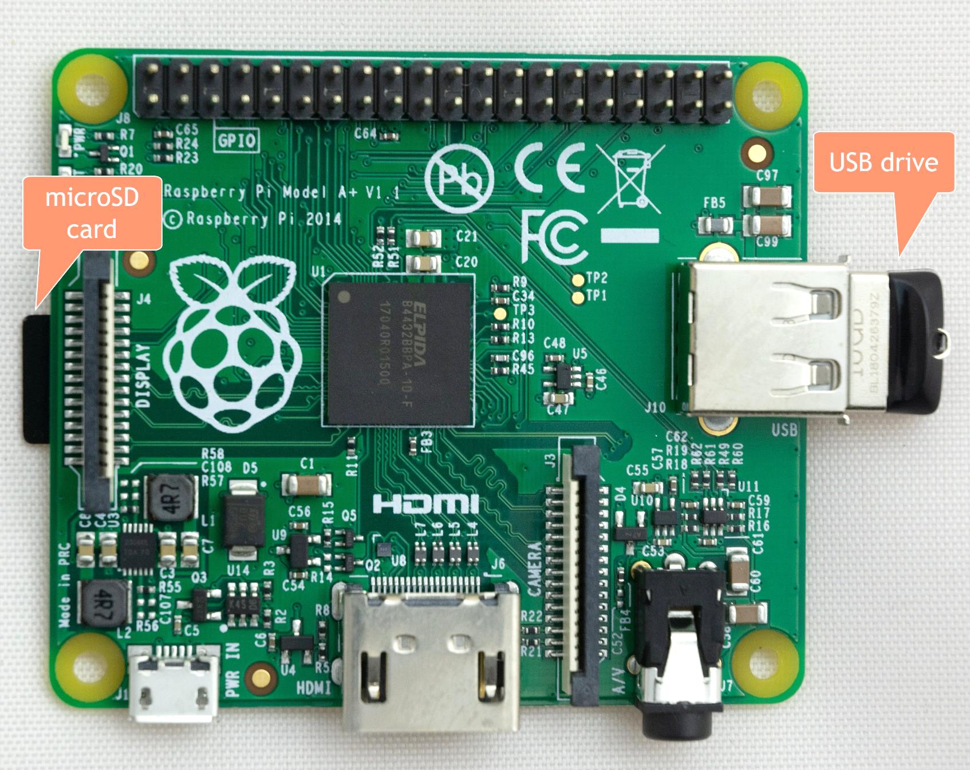
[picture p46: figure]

14

# STEP 9: Add Pi

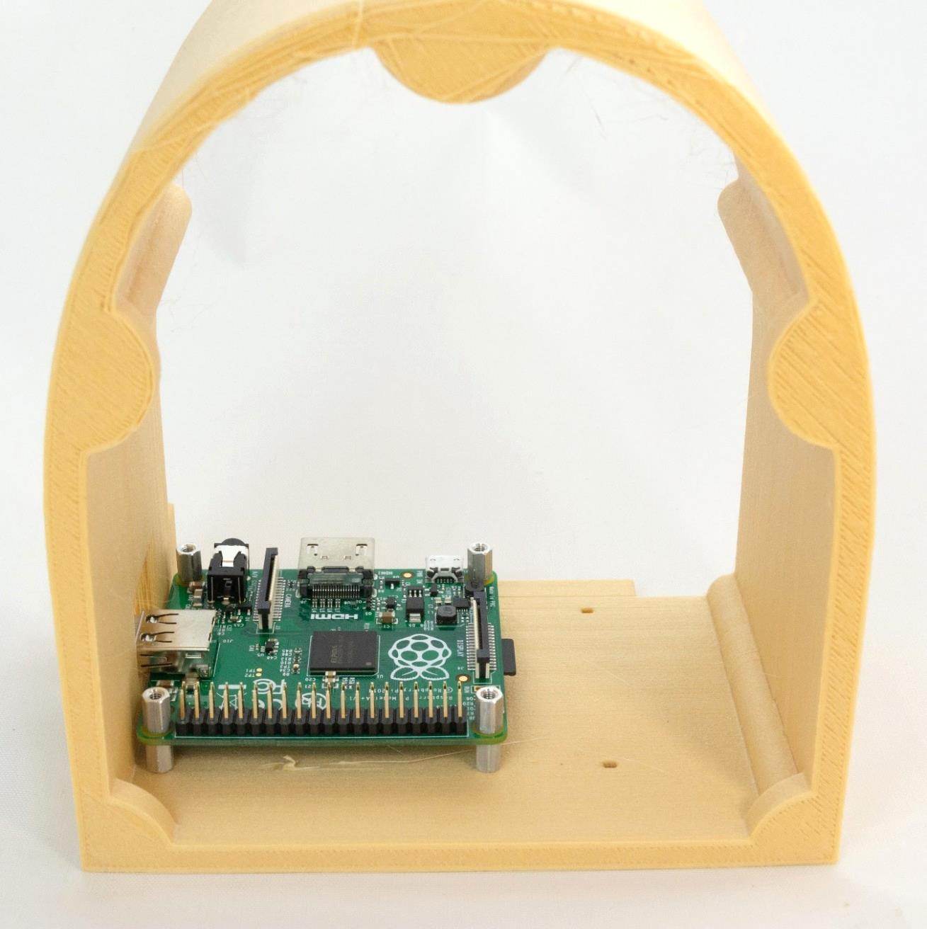
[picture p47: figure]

15

# STEP 10: Mount the Pi

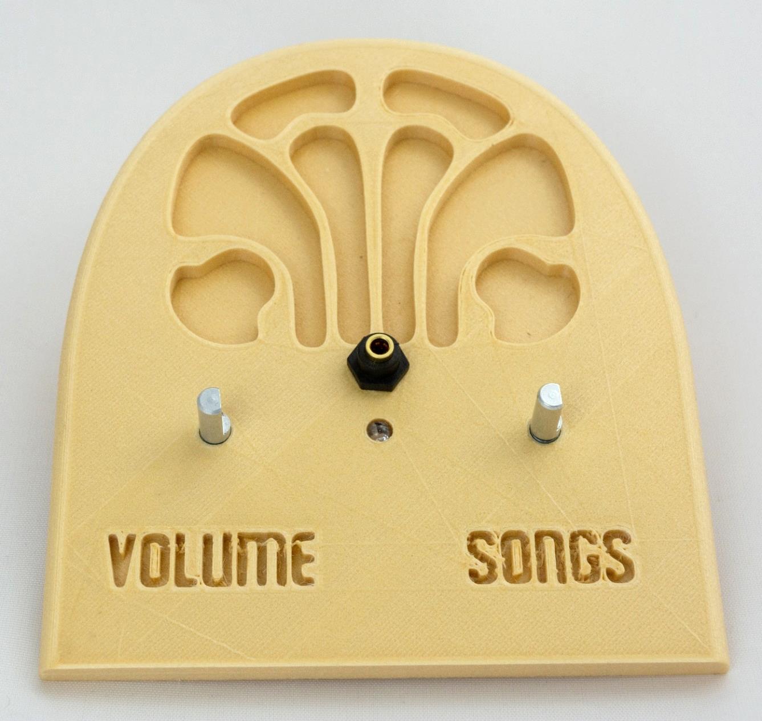
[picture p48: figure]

16

# STEP 11: Install the front panel components

Install the two rotary encoders (knobs), the LED, and the headphone jack. The rotary encoders need to be screwed in as far as they will go, or the button press won’t work – test the rotary encoders to make sure they rebound from a button press.

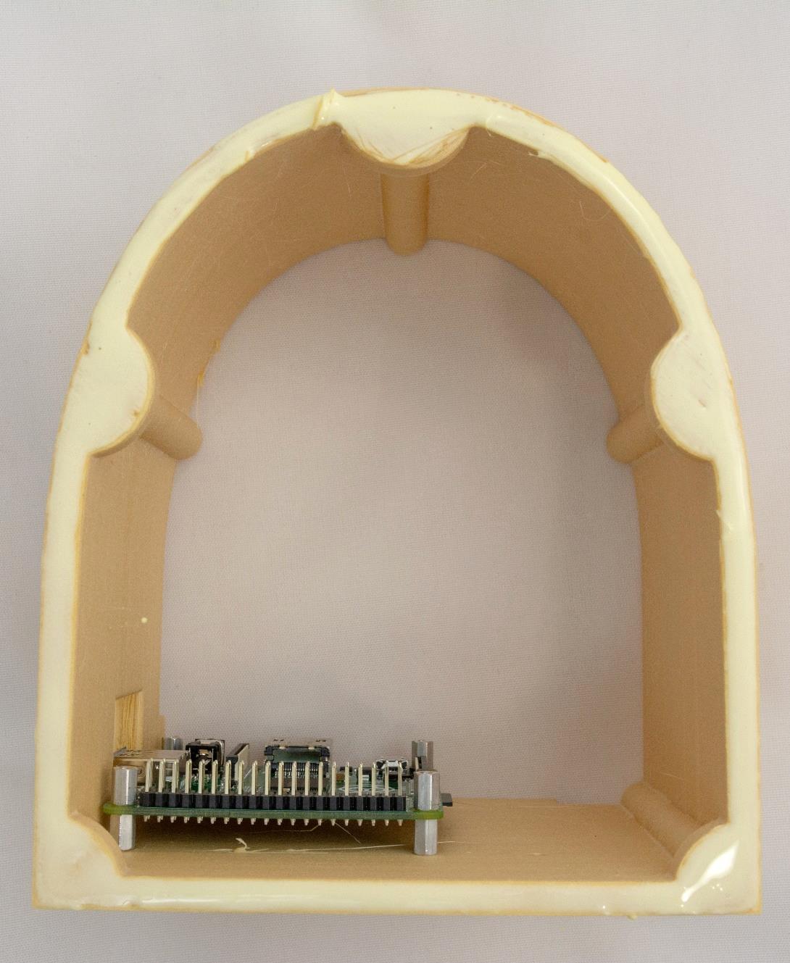
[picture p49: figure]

17

# STEP 12: Apply glue

Apply glue to the front of the body piece:

18

# STEP 13: Glue the face

Glue on the face, using painter’s tape to clamp:

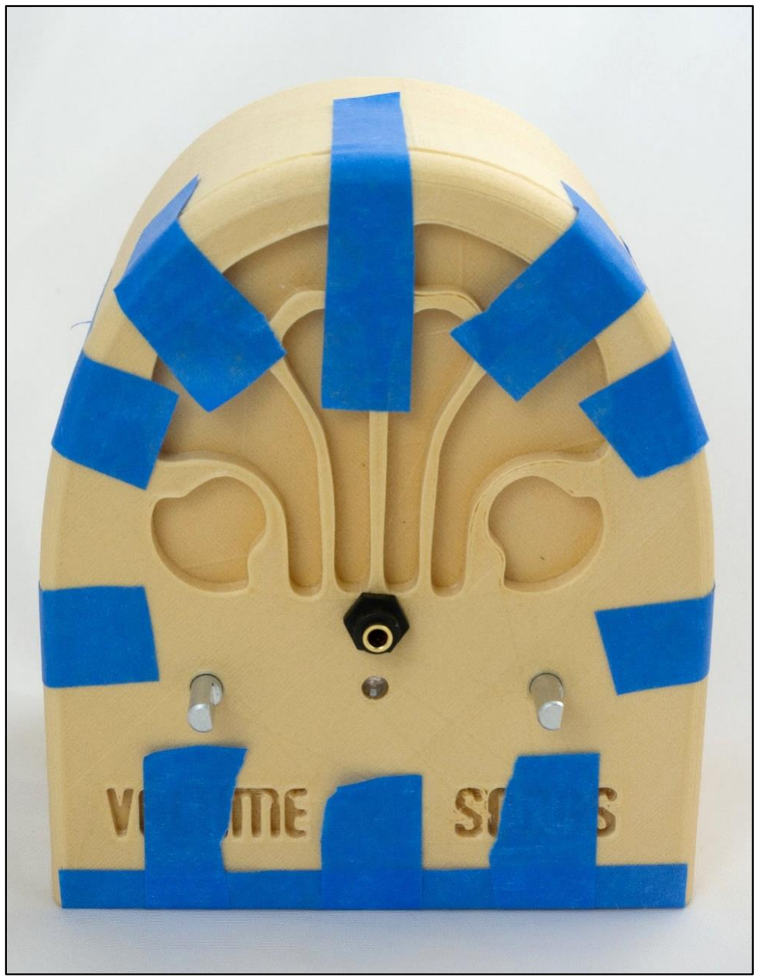
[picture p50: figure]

19

# STEP 14: Wire it

Attach wires from the knobs and the LED to the Raspberry Pi as per the diagram and photos below. No soldering required – just press the wires into place. This is where
most build errors happen, so please carefully check your work. | 1 3v3 Power 2 5v Power 3 GPIO 2 (SDA) 4 5v Power 5 GPIO 3 (SCL) 6 Ground 7 GPIO 4 (GPCLKO) 8 GPIO 14 (TXD) 9 Ground 10 GPIO 15 (RXD)

Songs knob (rotary encoder) ¹¹ GPIO 17 12 GPIO 18 (PCM_C) 13 GPIO 27 (PCM_D) 14 Ground 15 GPIO 22 16 GPIO 23 17 3v3 power 18 GPIO 24 19 GPIO 10 (MOSI) 20 Ground 21 GPIO 9 (MISO) 22 GPIO 25 23 GPIO 11 (SCKL) 24 GPIO 8 (CE0) 25 Ground 26 GPIO 7 (CE1) 27 ID_SD 28 ID_SC 29 GPIO 5 30 Ground 31 GPIO 6 32 GPIO 12 33 GPIO 13 34 Ground 35 GPIO 19 (MISO) 36 GPIO 16 37 GPIO 26 38 GPIO 20 (MOSI) 38 Ground 40 GPIO 21 (SCLK)

Volume knob (rotary encoder) | On/off indicator LED CLK | GND
+DT SWCLK GND
+DT SW
B
G

R

20

The result should be as you see it below. The front of the LED should be flush with the front of the face. If the LED is a bit loose, just use some glue.

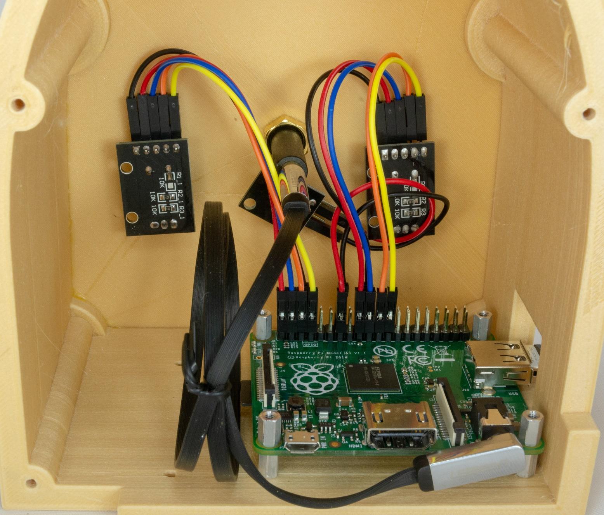
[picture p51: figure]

21

# STEP 15: Add audio cable

The audio cable goes from the back of the Pi to back of the front panel’s headphone jack:

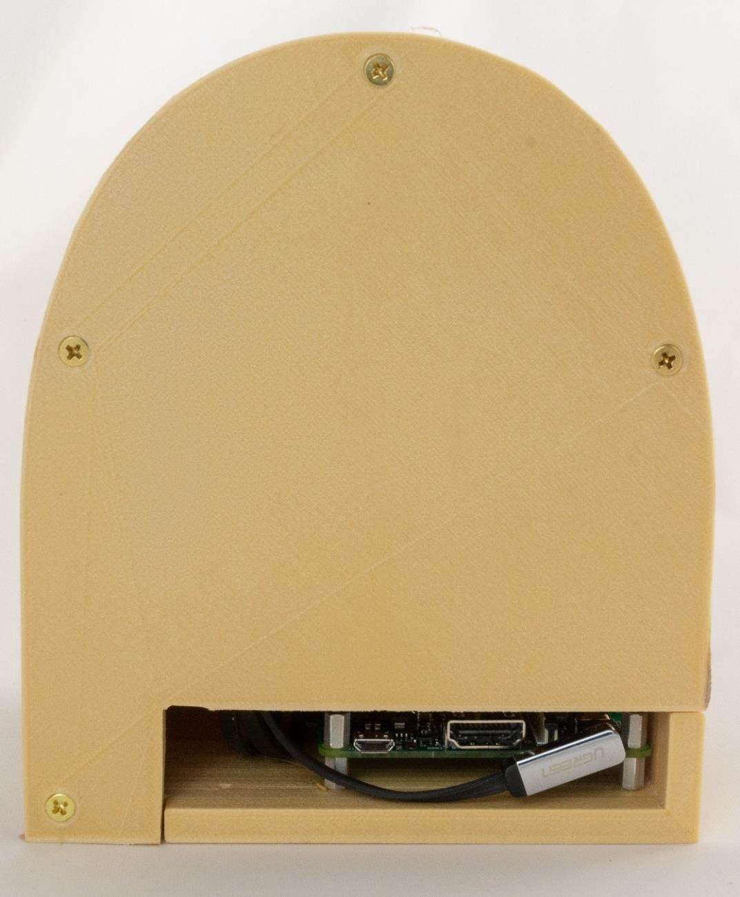
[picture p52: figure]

22

# STEP 16: Screw on the back

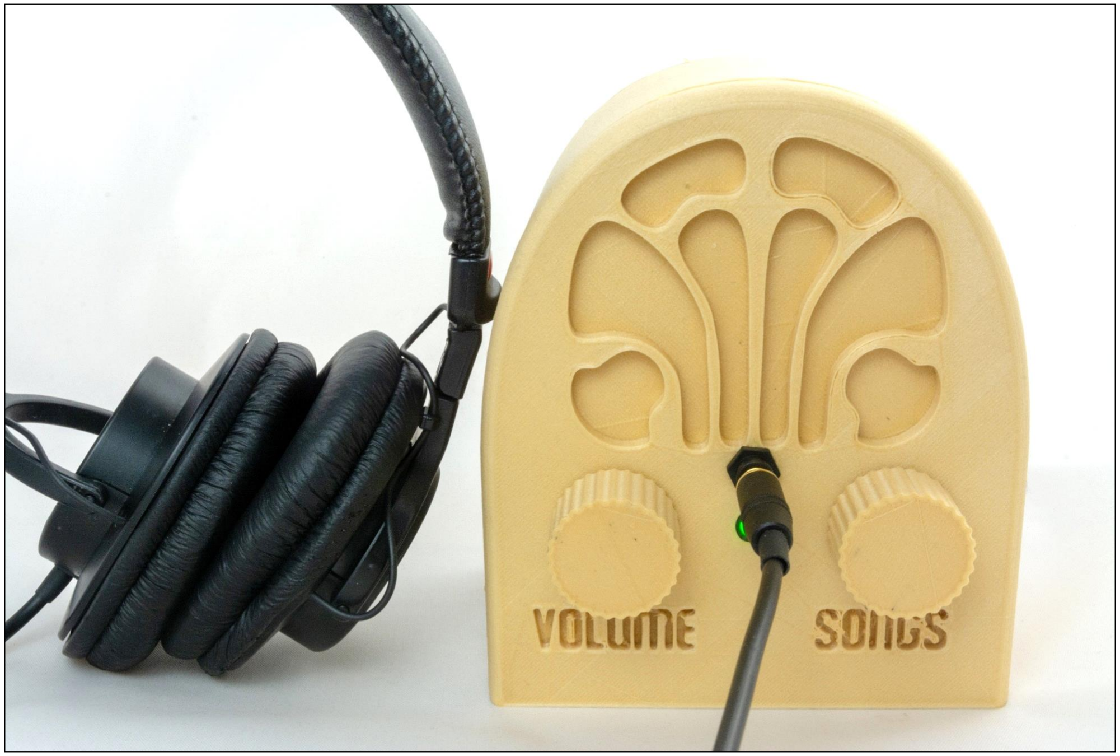
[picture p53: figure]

23

# STEP 17: Put on the knobs & enjoy

If the knobs don’t easily slide on the metal shafts, just heat the knobs up with a heat gun or hair dryer or (last resort) boiling water. You can also put some grease or cooking oil on the metal shafts.

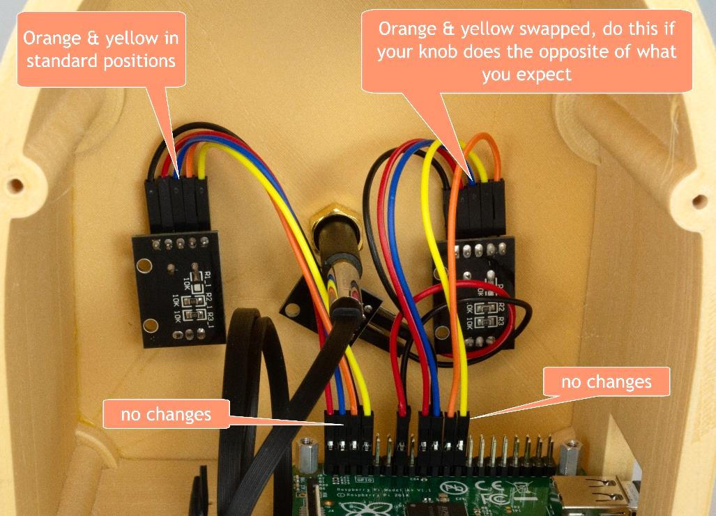
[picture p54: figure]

24

# STEP 18: Test it

Now that you have assembled everything, it is time to test.

Test | Description & Expectation
Light 20sec after power on | The indicator LED turns on when Dementia Friendly Music Player is ready to play music, which is generally about 15 seconds after power on.
Start song | Turning either of the knobs will start music playing.
Change song | Turn the songs knob. If you go forward and backward through the song list as expected, then all is well.
Change volume | Turn the volume knob. If the volume goes up and down as expected, then all is well.
Pause | Tap the volume knob, song should pause. Tap the songs knob, this should also pause the song.
Unpause | Tap a knob

## If one or both knows do the opposite of what you expect

Once assembled, you may find your knobs doing the opposite of what you expect e.g. a clockwise turn decreases the volume. This is because there are two kinds of rotary encoders out there. Happy, the fix is easy, just switch the orange and yellow wires on the misbehaving knob(s) (don’t touch the Pi itself):

25

# STEP 19: Tape on the instructions

Print this page and tape the instructions in the box below to the bottom of your new Dementia Friendly Music Player:

## To create personalized music

Organize the music on your computer
One folder per album. Use MP3 files, must have .mp3 file extension. Or iTunes files (.m4a). Or FLAC files (.flac). Optionally, use folder names prefixes to specify the play order e.g. A_, B_

Copy the music to the USB thumb drive
1. Unplug the Dementia Friendly Music Player.
2. Remove the USB thumb drive and place in your computer.
3. Copy music files from your computer to the USB thumb drive.
4. Put the USB thumb drive back in.
5. Plug in your Dementia Friendly Music Player.

## Congratulations!

Congratulations! You should have a fully functional Dementia Friendly Music Player.

## Let me know how it went

I’d love to hear how your build process went and if it was useful for the recipient. rosswesleyporter@gmail.com

26

## Appendix 1: Building 10+ at a time

Assumptions:

- You want to build 10 or more units at a time
- You are planning this far enough in advance (8 weeks or more) that you can order some of the parts directly from China
# units to make | 10

Item | Supplier | Quan | Each | Total | Per unit | Notes
Raspberry Pi 1 A+ single board computer (http://www.newark.com/raspberry-pi/raspbrry-moda-512m/silicon-manufacturer-broadcom/dp/81Y5333) | Newark | 10 | $20.00 | $200.00 | $20.00
Power supply (https://www.newark.com/pro-elec/28-19339/adaptor-ac-dc-5-1v-2-5a/dp/51AC7144) | Newark | 10 | $4.99 | $49.90 | $4.99
Panel mount 3.5mm headphone jack (http://www.newark.com/mcm/27-5937/3-5mm-inline-stereo-mount-female/dp/40T6284) | Newark | 10 | $2.69 | $26.90 | $2.69
Female-female jumper wires (https://www.aliexpress.com/item/32800215149.html?spm=a2g0s.9042311.0.0.6b164c4d50jzDO) | Ali Express | 10 | $0.60 | $6.00 | $0.60
M2.5 6mm thread + 6mm standoff screws (100 pieces) (https://www.aliexpress.com/item/32789600225.html?spm=a2g0s.9042311.0.0.27424c4dxaP132) | Ali Express | 1 | $1.98 | $1.98 | $0.20
Audio cable (https://www.aliexpress.com/item/32828101917.html?spm=a2g0s.9042311.0.0.6b164c4d50jzDO) | Ali Express | 10 | $2.79 | $27.90 | $2.79
KY-016 indicator LED (10 pieces) (https://www.aliexpress.com/item/32955003054.html?spm=a2g0s.9042311.0.0.6b164c4d50jzDO) | Ali Express | 1 | $1.92 | $1.92 | $0.19
KY-040 rotary encoders (knobs) (https://www.aliexpress.com/item/599712551.html) | Ali Express | 20 | $0.72 | $14.40 | $1.44
16GB+ micro SD card (https://www.amazon.com/gp/product/B06XWN9Q99/ref=ppx_yo_dt_b_asin_title_o05_s00?ie=UTF8&psc=1) | Amazon | 10 | $7.48 | $74.80 | $7.48
USB thumb drive (https://www.amazon.com/gp/product/B077Y149DL/ref=ppx_yo_dt_b_search_asin_title?ie=UTF8&psc=1) | Amazon | 10 | $7.19 | $71.90 | $7.19
#4 x 5/8” flat head wood screws (100 pieces) (https://www.amazon.com/Snug-Fastener-Stainless-Phillips-SNG107/dp/B07L4B9DHY) | Amazon | 1 | $7.30 | $7.30 | $0.73

| | | | | $48.30 | + tax + shipping

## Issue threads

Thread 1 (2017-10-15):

### ISSUE TITLE
Status LED without current limiting device

### ISSUE THREAD

**Issue by gnbl** [rosswesleyporter/dqmusicbox#1]
Nice project! Saw it on [Hackaday ](https://hackaday.com/2017/09/15/hackaday-prize-entry-dementia-friendly-music-player/) and came to check out the python control code and the SD write-protect.

I noticed that your "HDD LED" status indicator seems to be connected _directly_ to the Raspberry Pi GPIO.
Are these current limited outputs? It does not look like it: https://www.raspberrypi.org/documentation/usage/gpio/

So you should add a resistor or use an LED with integrated resistor that is designed for 3.3 V. Otherwise, the RPi and/or the LED could be damaged.

**Comment by rosswesleyporter** [comment]
Hi there. Thanks for checking out the project. And for taking the time to note the issue. To the best of my knowledge that is indeed an LED designed for 3.3V (originally for use on PC motherboard pins that didn't have a current limiting resistor). I spent a long time looking for an LED that is both 3.3V and pre-wired for jumper pins. Trying to make it super easy for people to build. No LED problems so far (I started building these about two years ago). But given your concern, I'll setup a test system and let it run constantly for a month.

Did you find what you were looking for regarding TMP_WRITE_PROTECT? I updated the build instructions a few weeks ago with a new appendix describing the process that I use.

**Comment by gnbl** [comment]
Ok, I don't know if HDD LEDs generally have a resistor installed or if these are on the motherboard. 
There probably is a method to test an LED for an integrated resistor.
But resistor LEDs are available (https://www.google.com/search?q=led+integrated+resistor), and then "Dupont" jumper wires could be used to connect without soldering.

Regarding the SD card: I did not know about the lock feature beforehand, though I've wondered what the Secure stands for. It's good to know, albeit as a last resort measure IMO. I've previously just tried to minimize logging to slow down the wear on the card but wanted to look into using the card as ROM and running the system from RAM alone. If I should manage to get anything working I can let you know.

**Comment by rosswesleyporter** [comment]
Just to be safe, I updated the plans to use an LED module with visible and sufficient resistors, specifically a KY-016 LED module.

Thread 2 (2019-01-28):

### ISSUE TITLE
dqmusicbox_v4_1 image not compatible with Raspberry Pi 3A+

### ISSUE THREAD

**Issue by scruss** [rosswesleyporter/dqmusicbox#2]
Since the 3A+ replaced the A+, the image in the instructions doesn't work. Needs an update to the firmware files in /boot from latest Raspbian

**Comment by rosswesleyporter** [comment]
Thanks for that. I think I tested with the 3A+ and it seemed to work fine. I'll check again.

**Comment by rosswesleyporter** [comment]
FYI, I just did a quick build of an image that works on a Pi 3A+. I'll do some testing with the aim to post it this weekend.

**Comment by rosswesleyporter** [comment]
Hello. I uploaded a new version of the image. Works on the Pi 3A+. Also tested on 1A+ and 3B+. And I made corresponding updates to the build instructions.  If you want to download the image: bit.ly/2UkYkl9

**Comment by scruss** [comment]
Thanks, Ross! The new image works well with my 3A+ box.

(I'm with Makers Making Change, by the way — based out of Toronto. We really appreciate what you've done with this device!)

**Comment by rosswesleyporter** [comment]
Glad to hear that it works. I love what Makers Making Change is doing. And
that reminds me that I need to update my Makers Making Change page with
info about the new model that includes speakers.

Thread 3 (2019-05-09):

### ISSUE TITLE
Making read-only SD card process easier

### ISSUE THREAD

**Issue by scruss** [rosswesleyporter/dqmusicbox#3]
In conversation with @ctyler recently, it seems that making the SD card filesystem read-only is much simpler than the way documented in [instructions](https://github.com/rosswesleyporter/dqmusicbox/blob/master/docs/build_instructions_bamboo.docx?raw=true)

**Comment by rosswesleyporter** [comment]
I'm all for simpler. Any links to the alternate method?

As you saw, the current method acts only on the SD card itself. Which carries the benefit that unplugging the unit acts as a factory reset.

**Comment by ctyler** [comment]
Will write some notes on this when time permits, which probably means first week in Feb.

**Comment by rosswesleyporter** [comment]
Thanks Chris. I'm all for simple. For when you have time, here are a few more notes about the current setup:

- The intent is longevity e.g. avoid SD corruption from unexpected shutdowns during writes.

- Because the software doesn't need to change over time, ROM-ish behaviour is fine. That is, the device does only one thing (plays music) and that music playing doesn't need to change over time.

- Also, the device does not need to be on a network of any kind, thus I'm not so concerned about security updates.

- Uses DietPi & RAM logging to reduce writes

- If the maker chooses, they can enable the TMP_WRITE_PROTECT mode on the SD's card specific data, which effectively write protects the whole card e.g. e.g. every power loss is a factory refresh. But it's a pain the in butt for makers to enable this using the process that I documented (though trivial for me now that I've done it a bunch of times).

**Comment by rosswesleyporter** [comment]
I removed the SD card write-protection steps from the build instructions as there seem to be issues with this in very recent versions of DietPi. It's not a super critical feature as I configured DietPI to reduce the likelihood of SD card corruption as a result of unexpected power loss e.g. by enabling RAM logging. I may later try some additional approaches in DietPi, now that it has explicitly added configuration options for read-only filesystems. But I'll close this specific issue.

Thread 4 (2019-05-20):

### ISSUE TITLE
3D printed dials are at an undefined size

### ISSUE THREAD

**Issue by scruss** [rosswesleyporter/dqmusicbox#4]
![tiny_dials](https://user-images.githubusercontent.com/425706/57396456-71d0fc80-7198-11e9-9c0b-7feae826ab49.jpg)
Even after scaling by 25.4 - as might happen if you'd sized these wrongly in inches - these are tiny.

Please provide at correct scale, also perhaps rotated flat so they're easier to print.

**Comment by rosswesleyporter** [comment]
Hello again. I'll check on these when I get home i.e. remind myself how I printed it. If I remember correctly, Cura auto scaled it by some power of ten e.g. 10x, 100x, 1,000x or something. Please note that 3D printing is not my expertise. I did the laser cut design and wrote the software. Chad @ Makers Making Change found a volunteer to do the 3D design (Blender). So I'm not sure if I'll be able to correct the scaling issue. But I can update the build instructions with the amount of auto scaling that Cura applied.

**Comment by rosswesleyporter** [comment]
Hi. Confirmed - Cura autoscaled 10,000% percent for me. I didn't have to do anything. But it sounds like this is not the case for the slicer that you (and probably others) are using. So I just updated the build instructions to note that manual in-slicer scaling may be necessary. The updated instructions are now live in github and on http://DementiaMusicPlayer.org. 

If you know of a way to correct the scaling in the STL file, I'm all ears. If I recall correctly, Trey (wonderful volunteer that Chad connected to the project) tried various Blender exports but the scaling issue persisted. Also if I recall correctly, I found posts from others also puzzled by similar issues with Blender exports in some circumstances.

**Comment by jakemcivor** [comment]
I manually corrected the stl file for the dials using Autodesk Meshmixer. I also re-oriented the other files so they are in the position best suited for printing.
#5

**Comment by rosswesleyporter** [comment]
Thanks Jake! Merged.

**Comment by rosswesleyporter** [comment]
I'm assuming that everything is working for you now. So I'll close this. BTW, one of the next things I'll be working on is updating the build instructions to focus on one-sitting builds, in preparation for a likely buildathon at the Bellingham Makerspace.

**Comment by scruss** [comment]
Yes, it did, thanks; slightly loose in PET-G on Makers Making Change's
Toronto Prusa, but nothing that tape won't fix. I was going to post
these as a PR, but I see my colleague Jake beat me to it. If these were
3mf files, it would retain some of your preferred slicing settings too.

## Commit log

2015-08-03 Cosmetic adjustments to case plans.
    Cosmetic adjustments to case plans.
2015-08-17 Tweaked size of cut for LED.
    Tweaked size of cut for LED.
2015-08-31 30 Aug 2015
    30 Aug 2015
    [dqmusicbox.xlsx]
2015-09-19 18 September 2015
    18 September 2015
    [dqmusicbox.xlsx]
2015-11-27 November 2016 design that removes need for soldering & software configuration.
    November 2016 design that removes need for soldering & software
    configuration.
    [dqmusicbox.xlsx]
2015-11-28 Changed to solderless indicator LED
    Changed to solderless indicator LED
2016-11-06 updated links
    updated links
    [dqmusicbox.xlsx]
2017-01-02 v1.2 - change to Pi built-in headphone jack
    v1.2 - change to Pi built-in headphone jack
    [dqmusicbox.xlsx]
2017-05-30 v4_beta1
    beta1 of v4. No code changes. There are substantial changes to the case,
    the parts, and the instructions. See changelog in instructions.
    [dqmusicbox.xlsx]
2017-07-04 v4.01
    No real changes, just housekeeping prior to releasing v4.01
    [dqmusicbox.xlsx]
2018-02-26 v4.01
    v4.01
    [dqmusicbox.xlsx]
2018-02-27 v4.01_5
    v4.01_5
    [dqmusicbox.xlsx]
2018-04-24 v4.1_1
    v4.1_1
    [dqmuiscbox_bamboo_v5.xlsx, dqmusicbox.xlsx]
2019-05-14 Reorient & scale stl files
    Transformed the stl files to their intended print orientation. Scaled the dials by 10,000
    [Back.stl, Body.stl, Dials.stl, Front.stl]
2019-12-07 Case for speaker model updated to compy with Ponoko standards
    Case for speaker model updated to compy with Ponoko standards. No user-visible changes.
2019-12-20 v4.2.1
    v4.2.1
    [DQMusicBox_cathedral_5point2mm_cherry.dxf, DQMusicBox_cathedral_5point7mm_cherry.dxf]
2020-01-19 removed uneeded files & template elements
    removed uneeded files & template elements
    [dqmuiscbox_6point7mm_bamboo_v5_part1.dxf, dqmuiscbox_6point7mm_bamboo_v5_part2.dxf]
2020-03-12 Support for building 10+ units
    [build_instructions_wood_headphonesOnly.xlsx]
2020-03-14 Added costing for making 10+ units
    Added costing for making 10+ units
    [build_instructions_3D_printed.xlsx, build_instructions_small_speakers_cherry.xlsx, build_instructions_wood_headphonesOnly.xlsx]
2020-03-15 Added case for speakers only model
    Added case for speakers only model
    [DementiaFriendlyMusicPlayer_6point7mm_Ponoko.xlsx]
2020-03-15 Added case plans for speaker only model
    Added case plans for speaker only model using 5.2mm cherry veneer MDF wood
    [DementiaFriendlyMusicPlayer_5pint2mm.xlsx]
2020-03-15 Added build instructions for speaker only model
    Added build instructions for speaker only model
    [build_instructions_wood_speakersOnly.xlsx]
2020-03-23 Edited for clarity
    Edited for clarity
    [build_instructions_wood_speakersOnly.xlsx]
2020-03-23 Updated for clarity
    Updated for clarity
    [build_instructions_3D_printed.xlsx, build_instructions_small_speakers_cherry.xlsx, build_instructions_wood_headphonesOnly.xlsx]
2020-04-13 file renaming for clarity
    file renaming for clarity
    [build_instructions_deluxe.xlsx, build_instructions_plus.xlsx, build_instructions_standard.xlsx, build_instructions_standard_3D_printed.xlsx]
2020-09-12 Updated parts list
    Updated parts list
    [build_instructions_standard.xlsx]
2020-09-20 Updated parts lists, updated folder names
    Updated parts lists, updated folder names
    [build_instructions_deluxe.xlsx, build_instructions_plus.xlsx]
2020-09-20 Updated folder names to better match product names
    Updated folder names to better match product names
    [Back.stl, Body.stl, Dials.stl, Front.stl]
2020-09-20 updated folder names and file names to better match product names
    updated folder names and file names to better match product names
    [DementiaFriendlyMusicPlayer_Deluxe_5point2mm.dxf, build_instructions_deluxe.xlsx, build_instructions_plus.xlsx]
2020-09-20 updated folder names and filenames to better product names
    updated folder names and filenames to better product names
    [dqmuiscbox_6point7mm_bamboo_v5.xlsx]
2020-09-20 updated file names & folder names to better match product names
    updated file names & folder names to better match product names
    [DementiaFriendlyMusicPlayer_plus_5point2mm.xlsx, DementiaFriendlyMusicPlayer_plus_6point7mm.xlsx]
2020-09-21 updated file names and folder names to better match product names
    updated file names and folder names to better match product names
    [build_instructions_plus.xlsx]
2020-10-01 Updated drawings & description to match Ponoko uploader
    Updated drawings & description to match Ponoko uploader
    [build_instructions_standard.xlsx]
2020-10-01 updated parts list, updated Ponoko instructions - switch from SVG file to EPS file
    updated parts list, updated Ponoko instructions - switch from SVG file
    to EPS file
    [build_instructions_plus.xlsx]
2020-10-01 updated parts list, including Ponoko pricing
    updated parts list, including Ponoko pricing
    [build_instructions_plus.xlsx, build_instructions_standard.xlsx]
2020-10-01 updated parts list, including pricing
    updated parts list, including pricing
    [build_instructions_deluxe.xlsx, build_instructions_standard.xlsx, build_instructions_standard_3D_printed.xlsx]
2020-10-02 Updated standard model 5.2mm to decrease laser time
    Updated standard model 5.2mm to decrease laser time
2020-10-12 Updated links to case files, removed old case file
    Updated links to case files, removed old case file
2021-03-06 update bill of materials
    update bill of materials
    [build_instructions_standard.xlsx]
2021-03-06 updated bill of materials
    updated bill of materials
    [build_instructions_standard_3D_printed.xlsx]
2021-03-07 update bill of materials
    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
    [build_instructions_deluxe.xlsx]
2022-03-26 updated link for laser cutting plans
    updated link for laser cutting plans
